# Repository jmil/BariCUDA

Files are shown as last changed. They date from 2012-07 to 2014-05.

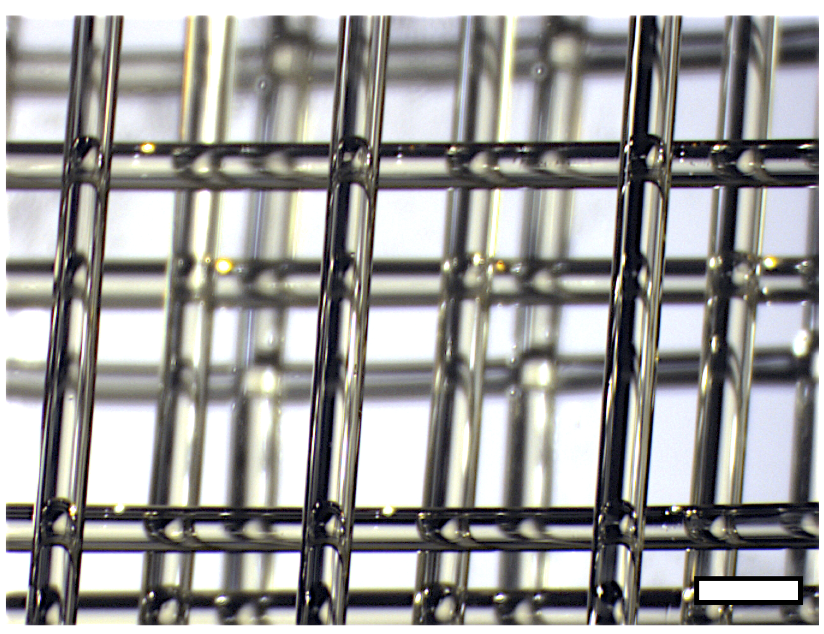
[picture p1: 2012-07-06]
MillerJS-03-3DPrintedSugar.png

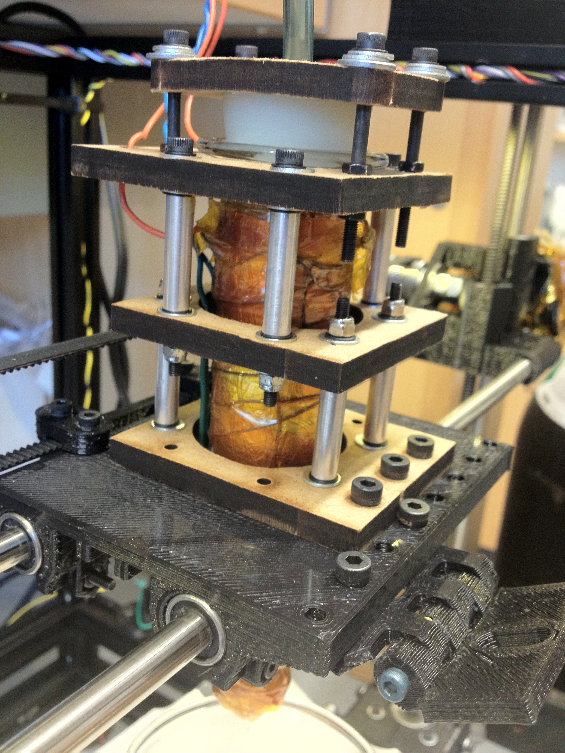
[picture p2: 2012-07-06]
SugarExtruder.jpg

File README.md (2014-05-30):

BariCUDA
========

License: GPL 3.0

BariCUDA -- air pressure driven (read BariC) Universal (it extrudes anything) Degree Amplifier (as in temperature)

by Jordan Miller http://twitter.com/jmil

As seen here:
http://www.thingiverse.com/thing:26343

See the BariCUDA used for precision pneumatic extrusion of sugar filaments for templating living vascular tissues for regenerative medicine:
http://www.youtube.com/watch?v=9VHFlwJQIkE

modified from MakerBot Frostruder MK2:
http://www.thingiverse.com/thing:1143

Introducing the BaricUDA Extruder.

Derived from the venerable MakerBot MK2 Frostruder, this air-pressure driven extruder ("baric") is a *U*niversal extruder because it adds a *D*egree *A*mplifier (yep... temperature) to let you extrude anything.

We used this to precisely extruder sugar templates for engineering vascular tissues for regenerative medicine research. See the details here:

You can use it for:
1) Molten Sugar Extrusion
2) Molten Chocolate Extrusion
3) Molten PLA and ABS and other experimental plastics Extrusion
3) Molten <insert your favorite thing here> Extrusion -- This is a *U*niversal Extruder! Any thermoplastic material can be extruded.

You are only limited by your motherboard and the number of MOSFETs you have (for control of pneumatics just like the Frostruder).

Operation is IDENTICAL to the Frostruder, you just need to add a heating element and thermistor for temperature measurement.

The Source Code and Files are Hosted on Github:
http://www.github.com/jmil/BariCUDA

NOTE: Sugar and Chocolate precision extrusion should be controlled NOT by precision of air pressure (which is hard) but instead by precision of temperature (which is easy). Temperature controls viscosity which controls extrusion rate at a given temperature.

The temperature to use depends on the material properties of your extrudate (read: the sugar). But you want around 100 degrees celsius extrusion for this type of sugar glass you can make at home (you DON'T need the cream of tartar):
http://www.wikihow.com/Make-Sugar-Glass

Chocolate is just as easy -- but don't use water! Chocolate and water don't mix.

RepRap does not support such a large extruder by default. You may need to first 3D print the additional Mendel vertices to widen the top of the Mendel so you can fit this extruder in there easily.

1. Get a Frostruder MK2 (you need the rubber stopper, tubing, and pneumatic solenoids)
2. Lasercut these new parts out of 1/4" MDF or other RIGID wood. It has to be really really stiff.
3. 3D print the RepRap holder for the extruder
4. Get the bolts, nuts, washers, and aluminum standoffs you need. I recommend locking nuts so that the fitting is tight.
5. Assemble and WIN!

NOTE: There's no BOM because it will depend on the thickness of the material you laser cut. I used 1/4" MDF and 50 mm screws with 25 mm aluminum standoffs. You should be able to figure it out by looking at the images in this Thing.

But the idea is you take the stopper clamp and top clamp and put the glass syringe in (I use Air-Tite.com). Then you wrap in foil and then wrap in nichrome and affix your thermistor. Then you put the stand-offs in and get the spacing you want with one or more spacer clamps. Then you should be all set.

I use one stopper clamp, one top clamp, one spacer clamp, and one bottom clamp.

The bottom clamp has the holes that affix it to the x-carriage on the RepRap. If you use 1/4" MDF it will be stiff enough to support the entire BariCUDA Extruder even while extruding. We have been using this design for more than a year and half with no problems.

Enjoy!

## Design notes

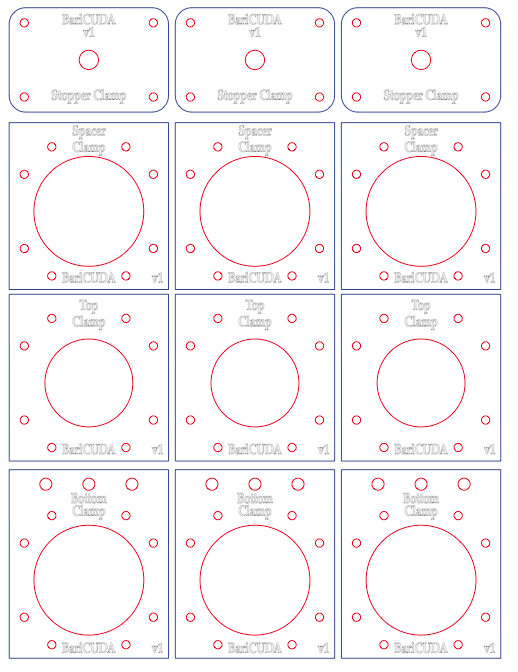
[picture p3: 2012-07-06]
jmil_Clamp_Screenshot.png

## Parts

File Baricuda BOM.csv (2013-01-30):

Part | Source | Part No. | Unit | Unit Price | Price | URL | Purpose/Notes
50 ft – 26 Gauge Nichrome 60 w/Double Glass Serve | pelicanwire | P2126N60DGS | 1 | 50 | 50
100 kOhm thermistor | ultimachine |  | 10 | 2.75 | 27.5 | http://ultimachine.com/content/thermistor-100k
2 pin terminal (crimping, soldering, stick in the hole) | ultimachine or OEDK |  | 1 | 2.5 | 2.5 | http://ultimachine.com/content/254mm-1x2-connector-housing-kit-6-pack | connecting thermistor to motherboard
25 - Zinc-Plated Alloy Steel M3 50 mm screws | McMaster Carr | 91290A137 | 4 | 4.91 | 19.64 | http://www.mcmaster.com/#catalog/118/3121/=j61hb4
100 - Zinc-Plated Alloy Steel M3 20 mm screws | McMaster Carr | 91290A123 | 1 | 6.47 | 6.47 | http://www.mcmaster.com/#catalog/118/3121/=j61hb4
Al Standoffs, 25mm, fits M3 | McMaster Carr | 94669A027 | 8 | 1.5 | 12 | http://www.mcmaster.com/#catalog/118/3257/=j61kk1
50 - Metric Type 316 SS Nylon-Insert Hex Locknut M3 Size, .5mm Pitch, 5.5mm Width, 4mm Height | McMaster Carr | 94205A220 | 4 | 4.75 | 19 | http://www.mcmaster.com/#catalog/118/3197/=j6ajwr
50 - M3 Metric Hex Nuts | McMaster Carr | 94150A325 | 2 | 3.08 | 6.16 | http://www.mcmaster.com/#94150A325
100 - 316 Stainless Steel M3 Washers | McMaster Carr | 90965A130 | 1 | 1.76 | 1.76 | http://www.mcmaster.com/#90965A130
100 - 316 Stainless Steel M4 Washers | McMaster Carr | 90965A150 | 1 | 2.43 | 2.43 | http://www.mcmaster.com/#90965A150
50 - 316 Stainless Steel M4 nuts | McMaster Carr | 94150A335 | 2 | 3.42 | 6.84 | http://www.mcmaster.com/#94150A335
100 - 12.9 Alloy Steel M4 25 mm screws | McMaster Carr | 91290A176 | 1 | 8.14 | 8.14 | http://www.mcmaster.com/#91290A176
Air-tite 50 mL glass syringe | Air-Tite | GL50 | 1 | 31.95 | 31.95 | http://www.air-tite-shop.com/p-34-glass-syringe-metal-luer-lock-tip.aspx
silicone or rubber stopper (#8 or #9 size) | Chem Stockroom |  |  |  | 0
18 gauge steel nozzle luer lock | Nordson EFD - custom quote | KIT, TIP 18GA .033"(.84MM)X1/2" SS, 5PC | 1 | 36.54 | 36.54
1/4” wide Kapton Tape | ultimachine | UMKPTON025 | 5 | 8 | 40 | http://ultimachine.com/content/dupont-kapton-high-temp-adhesive-tape-14
1' Ceramic Insulation Tape | ultimachine | UMCERTAPE | 5 | 1.5 | 7.5 | http://ultimachine.com/content/ceramic-insulation-tape
3 Way 2 Position Solenoid Air Valve 1/4" NPT 12V DC | ebay | Item# 190444504454 | 1 | 29.84 | 29.84 | http://cgi.ebay.com/ws/eBayISAPI.dll?ViewItem&item=190444504454 | only works at 10-20 psi minimum, but CHEAP!
10 – PC Swift Push Lock Straight Fittings 1/4"OD- 1/4"NPT | ebay | Item# 260477680739 | 1 | 7.8 | 7.8 | http://cgi.ebay.com/ws/eBayISAPI.dll?ViewItem&item=260477680739
1/4" polyurethane Tubing |  | Item # 260505968939 | 1 | 22.35 | 22.35 | http://cgi.ebay.com/ws/eBayISAPI.dll?ViewItem&item=260505968939
tube cutter |  | Item # 260489803800 | 1 | 6.7 | 6.7 | http://cgi.ebay.com/ws/eBayISAPI.dll?ViewItem&item=260489803800
0.5" acrylic from pattern (laser cut) | MW has extra material |  |  |  | 0
25 – 12.9 Alloy Steel M3 40mm socket head screws | McMaster Carr | 92290A128 | 2 | 3.63 | 7.26 | http://www.mcmaster.com/#socket-head-cap-screws/=j6anv3
 |  |  |  |  | 0
X-CARRIAGE |  |  |  |  | 0
4 of 8 mm LM8UU linear bearings | Ebay |  | 1 | 7 | 7 | http://www.ebay.com/itm/10pcs-LM8UU-8mm-Linear-Ball-Bearing-Bush-Bushing-/290638920863?pt=LH_DefaultDomain_0
4 25 mm m3 screws and nuts | McMaster Carr |  |  |  |  |  | covered in above lines
Printed X-Carriage Part | MW has material
 |  |  |  | TOTAL | 359.38

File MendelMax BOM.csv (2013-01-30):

PLEASE NOTE: A kit with all items marked with an X or "Upgraded" in column C is available from http://store.mendelmax.com/mendelmax-hardware-kit/
Item | Category | In MM.com kit | Part Number | Source | Qty Required for build | Order qty of pt number | Price Each | extended | Needed for | Notes
10mm M5-.80 screws, bag of 100 | Hardware | x | 91292A124 | McMaster | 100 | 1 | $7.68 | $7.68 | MendelMax | You need exactly 100 of these screws for a standard build, so I recommend you buy a spare bag. If you only get one bag, you can probably source individual replacement screws at Fastenal or another local source, but they are at a substantial premium. You will almost certainly need spares to add accessories. I prefer stainless steel for purely aesthetic reasons, but you can save a couple dollars by using Zinc or Black Oxide. I recommend Socket Head screws, but phillips or other M5-.8 machine screws will also work, but they are more fiddly to assemble.
608ZZ Bearings | bearings | x | 608ZZ10 | VXB.com | 7 | 7 | $0.50 | $3.50 | MendelMax | 2 each are used for the X & Y idlers, 3 for the Wade's extruder. You will also need four if you use the suggested filament spool. Part number is for a 10 pack for $5, you may want to buy a larger package, these bearings are used in many reprap related projects.
8mm Thrust Bearing | bearings | Not needed | 6655K54 | McMaster | 2 | 2 | $2.79 | $5.58 | MendelMax | These are optional, and are used to support the weight of the Z axis from the base of the printer, instead of from the motor shafts. This should improve reliability and extend motor life. You can safely leave these off if you prefer, and there is little benefit if you are using high quality Z couplers.
8mm Drill Rod 36" or 1M | hardware | upgraded | 88625K67 | McMaster | 3 | 3 | $5.13 | $15.39 | MendelMax | You can use 8mm or 5/16", and any formula of drill rod (Called "Silver Steel" in some parts of the world). Type O1 or W1 is usually cheapest and are perfectly suited to what we need. Stainless is also fine, but is considerably more expensive. Plain steel rods from a hardware store are not recommended, and zinc coated rods are not suitable.
M3 or SAE #6 washers | hardware | x | 90126A509 | McMaster | 20 | 1 | $1.27 | $1.27 | MendelMax | McMaster part is for a box of 100. Single parts are likely at least $.05 each, so it is most cost effective to just buy 100.
Wade's Idler Stud | hardware |  | 90435A120 | McMaster | 1 | 1 | $0.30 | $0.30 | Wade's | Not required if you have a cutoff of M8 from your threaded rod, but for $.32 saves the effort of an extra cut.
M5 nuts, box of 100 (Thin nuts preferred) | hardware | x | 90695A037 | McMaster | 1 | 1 | $2.78 | $2.78 | MendelMax | You only need a few for the assembly, but it is best to buy 100. Zinc coated is fine. Thin nuts are preferable to normal nuts since they can be used in place of t-slot nuts in a pinch, and even used as post-install nuts (they can be inserted through the top of the slot after the bot is assembled).
M3-.50, 10mm long | hardware | x | 91290A115 | McMaster | 20 | 1 | $4.48 | $4.48 | MendelMax | McMaster part is for a box of 100. Single parts are likely at least $.25 each, so it is most cost effective to just buy 100.
20-25mm M5 screws | hardware | x | 91292A128 | McMaster | 8 | 1 | $0.25 | $0.25 | MendelMax | You need 8, but I recommend just getting a box, they will be handy for future projects. Again, Stainless and the screw head type are specified only for looks, any similar screw will work.
M5 or #10 Washers, box of 100 | Hardware | x | 92141A011 | McMaster | 84 | 1 | $2.33 | $2.33 | MendelMax | Either M5 or SAE #10 washers will work. I use SAE #10 because they are slightly cheaper in the US. I use stainless for purely aesthetic reasons.
8mm or 5/16" threaded rod, 36" or 1M | hardware | upgraded | 98847A030 | McMaster | 1 | 1 | $3.89 | $3.89 | MendelMax | Plain steel or stainless will work, but stainless is recommended. Do not use zinc coated rod, as the zinc can lead to binding.
GT2 Belt | Belts | x | A 6R51M497060 | SDP-SI.com | 2 | 2 | $6.81 | $13.62 | MendelMax | Suitable pulleys & belts are also available from Misumi, but are considerably more expensive.
GT2 Pulleys | Belts | x | A 6Z51M036DF0605 | SDP-SI.com | 2 | 2 | $5.84 | $11.68 | MendelMax
Linear Bushings | bearings | x | A 7Z44MPSD08MAF | SDP-SI.com | 12 | 12 | $1.48 | $17.76 | MendelMax | After much debate, I have switched the recommended bushings from the previous Igus bushings, to a much easier to use Self Aligning bushing from SDP. Thease are a bit more expensive, but they are basicalaly foolproof, whereas the Igus bushings required a fairly high-precision mounting block that was difficult to reproduce accurately on a RepRap. MANY other choices are available, including LM8UU's, printed bushings, etc, but this is a good, inexpensive bushing that is very well suited to our application. Please note, SDP offers similar Bronze bushings that are a great choice with precision linear shafting, but are not recommended with drill rod.
300mm extrusions | Extrusions | x | HFS5-2020-300 | Misumi | 4 | 4 | $1.71 | $6.84 | MendelMax
340mm Extrusions | Extrusions | x | HFS5-2020-340 | Misumi | 4 | 4 | $1.93 | $7.72 | MendelMax
420mm extrusions | Extrusions | x | HFS5-2020-420 | Misumi | 6 | 6 | $2.39 | $14.34 | MendelMax
T-Slot nuts, bag of 100 | Extrusions | x | HNKK5-5 | Misumi | 1 | 1 | $19.32 | $19.32 | MendelMax
Blind Joint Screws | Extrusions | x | HTJ5 | Misumi | 4 | 4 | $0.62 | $2.48 | MendelMax
Pololu A4988 Stepper driver | electronics |  | http://www.lulzbot.com/en/24-pololu-a4988-stepper-motor-driver.html | Lulzbot.com | 4 | 4 | $16.00 | $64.00 | RAMPS | Also available from Pololu.com or Ultimachine.com. You need four, but having a spare on hand is not a bad idea.
NEMA 17 Motor | motors |  | http://www.lulzbot.com/en/48-nema-17-stepper-motors.html | lulzbot.com | 4 | 4 | $18.00 | $72.00 | MendelMax | http://ultimachine.com/content/kysan-1124090-nema-17-stepper-motor is also suitable. Desired specs: NEMA17 size, 1.5A or less, 8 mH inductance or less, 62oz.in (44Ncm, 4.4kg.cm) or more of torque, 1.8 or 0.9 degrees per step (200/400 steps/rev respectively)
RAMPS electronics | electronics |  | http://www.lulzbot.com/en/49-ramps-14-assembled.html | Lulzbot.com | 1 | 1 | $85.00 | $85.00 | RAMPS | Ultimachine.com is also an excellent choice
1" heat proof spacers | hardware | Not needed |  | hardware store | 4 | 4 | $0.25 | $1.00 | Y-axis | Used to rigidly separate the top and bottom plate, Should be heat resistant and preferably not heat conductive. I use hardwood.
12V 30A power Supply | Electronics |  |  | ebay | 1 | 1 | $37.00 | $37.00 |  | 30A is WAY more than you need, even with a 12V Heated Build Platform, but it should last longer if used well under it's specified rating, and the difference in price for an extra 10A is only about $10. You can safely use anything as low as 12V 6A with a 120V HBP and 15A with a 12V HBP. http://www.ebay.com/itm/New-12V-DC-30A-350W-Regulated-Switching-Power-Supply-MW-/120692623020?pt=LH_DefaultDomain_0 is a known good US seller, but there are other options on ebay that may be better for international buyers. Search for "12V 30A power supply". With a 30A supply, I happily run two RepRaps from a single power supply.
Aluminum sheet, 9..75x6x0.1" or 1/8" | Metal | Upgraded |  | OnlineMetals.com | 1 | 1 | $7.02 | $7.02 | Y-axis | Y-axis carriage plate, see above.
Aluminum sheet, 9.75x11x0.1" or 1/8" | Metal | x |  | OnlineMetals.com | 1 | 1 | $12.87 | $12.87 | Y-axis | Y-axis table, scale as needed. May be cheaper if sourced locally. Other materials are possible, but this is my preferred table design. Alloy is irrelevant, the quoted price is for 3003, which is usually the cheapest.
Arduino MEGA 1280 or 2560 | electronics |  |  | ebay.com | 1 | 1 | $30.00 | $30.00 | RAMPS | Either the 1280 or 2560 works fine, I recommend the 1280.
Heated Build Platform | Electronics | Upgraded |  | Ultimachine.com | 1 | 1 | $50.00 | $50.00 | Y Axis | The MendelMax has a slightly larger buld area than a Prusa, but you can use a standard Prusa HBP screwed to the bottom of an aluminum heat spreader. Using a Silicone heater such as McMaster #35765K55 works great too, but requires some expert advice, so consult #mendelMax before ordering.
Hobbed bolt | hardware |  |  | lulzbot.com | 1 | 1 | $7.00 | $7.00 | Wade's | It is possible to DIY as well, but for $7 it is not worth the effort.
Hot End | Hot End |  |  | Makergear | 1 | 1 | $75.00 | $75.00 | MendelMax | http://www.makergear.com/products/operators-pack I recommend the .5mm for 3mm filament to start with.
M5-30mm screws | hardware | x | 92125A220 ($7.85 for 25pk) (McMaster Carr) | hardware store | 4 | 4 | $0.30 | $1.20 | Y-axis | Used to connect the two plates. I recommend flat head screws, but you will need to countersink your top plate to use these. You can buy a countersink at your local hardware store. These allow you to set the screw tops flush with the table surface so you will not crash into the screws.
M8 or 5/16" Nuts | hardware | x | Square: 96887A322 ($5 for 25 pk) Hex: 91828A410 ($9.98 for 50pk) | Hardware store | 8 | 8 | $0.25 | $2.00 | MendelMax | Any suitable nuts from your local hardware store. Do not use Zinc coated, either plain steel or stainless is fine, and the material does not need to match your rods.
M8 or 5/16" screw or bolt, 25-30mm long | hardware | x | 91292A192 ($6.35 for 50) | Hardware store | 2 | 2 | $0.50 | $1.00 | MendelMax | Used to mount the the idler bearings on the X & Y axes. You may be able to use leftovers of your threaded rod, in which case you will need two extra nuts above. In the US, you can get these at Fastenal for $0.48 each: http://www.fastenal.com/web/products/detail.ex?sku=73496&ucst=t Again, I use Stainless for aesthetic reasons, but any finish or type of screw will work here as long as it is the right size.
M8 or 5/16" washers | Hardware | x | 90126A030 | hardware store | 4 | 4 | $0.25 | $1.00 |  | Used for the idlers. If you build the optional filament spool mount you will need an additional four.
NEMA 17 Motor | motors |  |  | lulzbot.com | 1 | 1 | $18.00 | $18.00 | Wade's | An additional stepper is required if you are using a Wade's extruder.
Printed Parts | RP |  |  |  | 1 | 1 | $85.00 | $85.00 | MendelMax | Lulzbot.com is selling sets, other sources should be available as well. http://www.lulzbot.com/en/plastic-parts/61-mendelmax-plastic-parts.html
Wade's extruider hardware | hardware |  |  | Hardware store | 1 | 1 | $5.00 | $5.00 | Wade's | Misc hardware required by the Wade;s extruder. Since you only need one or two of each, it is best to source these locally. See http://reprap.org/wiki/Wade%27s_Geared_Extruder for the full list. The bearings, hobbed bot (m8-50mm) and the screws and washers for the motor are already in this list.
Z Shaft couplers | hardware | x |  | ebay.com | 2 | 2 | $5.00 | $10.00 | MendelMax | http://www.ebay.com/itm/CNC-5x8mm-Motor-Shaft-Coupler-5mm-8mm-Coupling-/180707733213?pt=LH_DefaultDomain_0 You can also print your own couplers, but I have found printed couplers are considerably less reliable. Printed couplers should work much better if you use the thrust bearings listed above.
 |  |  |  |  |  |  |  | $515.00
 |  |  |  |  |  |  |  | $0.00
 |  |  |  |  |  |  |  | $0.00
 |  |  |  |  |  |  |  | $0.00
MendelMax 1.5 |  |  |  |  |  |  |  | $0.00
Item Number | Quantity | Part Number | Part Name | Configuration Name | Part Type | Revision | Comment | $0.00
1 | 4 |  | 608zz |  | Hardware |  |  | $0.00
2 | 2 |  | Acme_Leadscrew |  | Hardware |  |  | $0.00
3 | 2 |  | Bearing_Mount |  | Laser Cut |  |  | $0.00
4 | 2 |  | Cross Member |  | Laser Cut |  |  | $0.00
5 | 4 |  | HFS5-2020-300 |  | Extrusion |  |  | $0.00
6 | 4 |  | HFS5-2020-340 |  | Extrusion |  |  | $0.00
7 | 6 |  | HFS5-2020-420 |  | Extrusion
8 | 1 |  | Insulation |  | Hardware
9 | 2 |  | Insulation Clip |  | Laser Cut
10 | 2 |  | Lower Vertex Lower | Right | RP
11 | 2 |  | Lower Vertex Lower | Left | RP
12 | 2 |  | Lower Vertex Upper | Right | RP
13 | 2 |  | Lower Vertex Upper | Left | RP
14 | 12 |  | m3 no6 washer |  | Hardware
15 | 14 |  | m3 Socket Head Cap Screw | 10mm | Hardware
16 | 94 |  | m5 Socket Head Cap Screw | 10mm | Hardware
17 | 4 |  | m5 Socket Head Cap Screw | 22mm | Hardware
18 | 2 |  | m5 Socket Head Cap Screw | 12mm | Hardware
19 | 9 |  | m5 Socket Head Cap Screw | 20mm | Hardware
20 | 90 |  | m5_no10_washer |  | Hardware
21 | 4 |  | m5-10 flat head |  | Hardware
22 | 2 |  | m5-m6_35mm coupler |  | Hardware
23 | 66 |  | m5-misumi nut-hnkk5-5 |  | Hardware
24 | 29 |  | M5-thin nut |  | Hardware
25 | 3 |  | M8 Washer |  | Hardware
26 | 2 |  | m8-30 |  | Hardware
27 | 2 |  | M8-nut |  | Hardware
28 | 2 |  | MendelMax Leadscrew Nut |  | Hardware
29 | 1 |  | MendelMax Table |  | Custom
30 | 4 |  | NEMA17_47mm_deep |  | Motors
31 | 1 |  | Rod_mount_fixed |  | Laser Cut
32 | 1 |  | Rod_mount_float |  | Laser Cut
33 | 4 |  | Self Aligning Bushing | 10mm | Hardware
34 | 12 |  | Self Aligning Bushing | 8mm | Hardware
35 | 2 |  | Shaft, 10mm | 405mm | Hardware
36 | 2 |  | Shaft, 8mm | 445mm | Hardware
37 | 2 |  | Shaft, 8mm | 420mm | Hardware
38 | 1 |  | Silicone Heater |  | Electronics
39 | 2 |  | Table Support |  | Laser Cut
40 | 2 |  | Table_attachment |  | Laser Cut
41 | 2 |  | Top_Vertex_X | Logo | RP
42 | 2 |  | Top_Vertex_X | No Logo | RP
43 | 1 |  | X End Clamp for MendelMax Leadscrew |  | RP
44 | 1 |  | X End Idler for MendelMax Leadscrew |  | RP
45 | 1 |  | X End Motor for MendelMax Leadscrew |  | RP
46 | 1 |  | Y_Motor_Mount |  | RP
47 | 1 |  | Y-Idler-mount |  | RP
48 | 1 |  | Y-Idler-tensioner |  | RP
19 | 1 |  | Y-rod_mount_jig |  | Laser Cut
50 | 2 |  | Z_lower_motor_mount_10mm |  | RP
51 | 2 |  | Z_lower_motor_mount_10mm_support | Normal | RP
52 | 2 |  | Z_lower_motor_mount_10mm_support | Mirrored | RP
53 | 4 |  | Z_rod_clasp |  | RP
54 | 2 |  | Z_Top_Vertex_10mm_New |  | RP

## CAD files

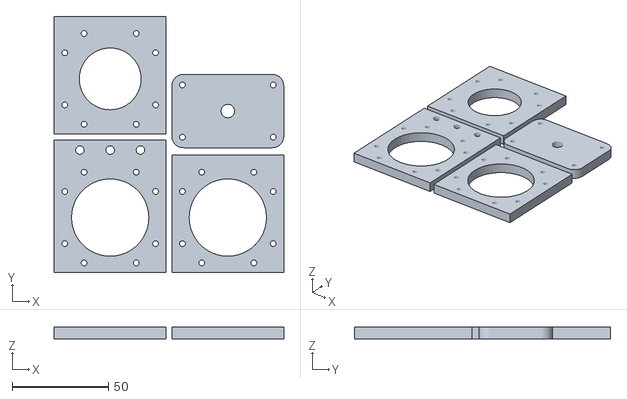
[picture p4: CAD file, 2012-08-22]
Baricuda_v1_LaserCutParts.stl
119.1 x 132.7 x 6.00

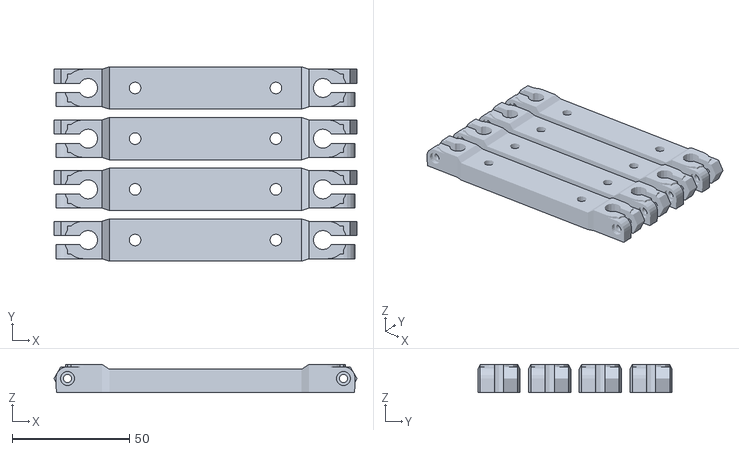
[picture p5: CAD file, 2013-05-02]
modifiedMendelMax1.5/Compact_MendelMax_Y-Rod_Holders/jmilYRodHolderfor8mmSmoothRods4off_fixed.stl
129.1 x 82.8 x 12.0

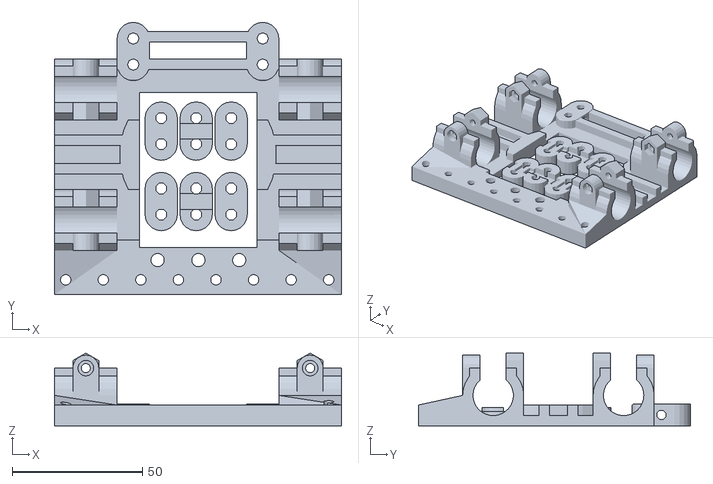
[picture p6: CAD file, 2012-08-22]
BariCUDA RepRap Holder with Fan Mount.stl
110.0 x 104.4 x 27.9

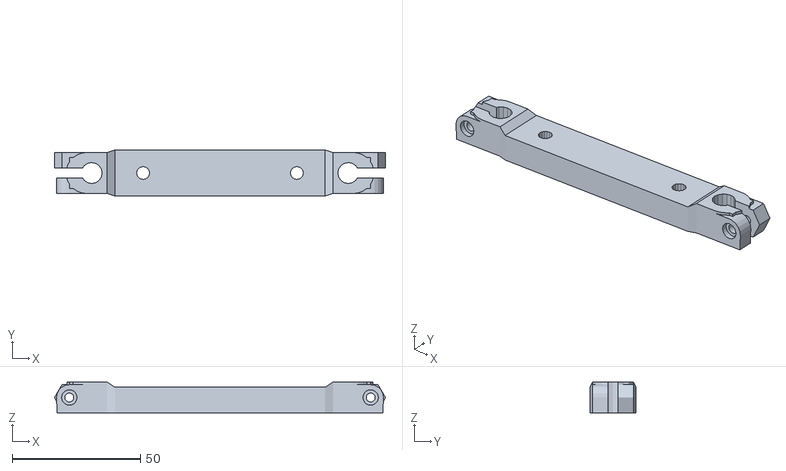
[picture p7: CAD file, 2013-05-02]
modifiedMendelMax1.5/Compact_MendelMax_Y-Rod_Holders/jmilYRodHolderfor8mmSmoothRods_fixed.stl
129.1 x 18.0 x 12.0

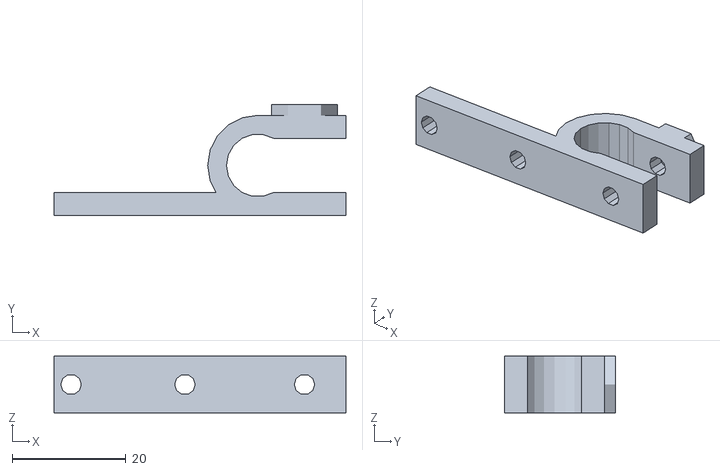
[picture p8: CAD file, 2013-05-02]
modifiedMendelMax1.5/endstop-holder_10mm.stl
51.3 x 19.5 x 10.0

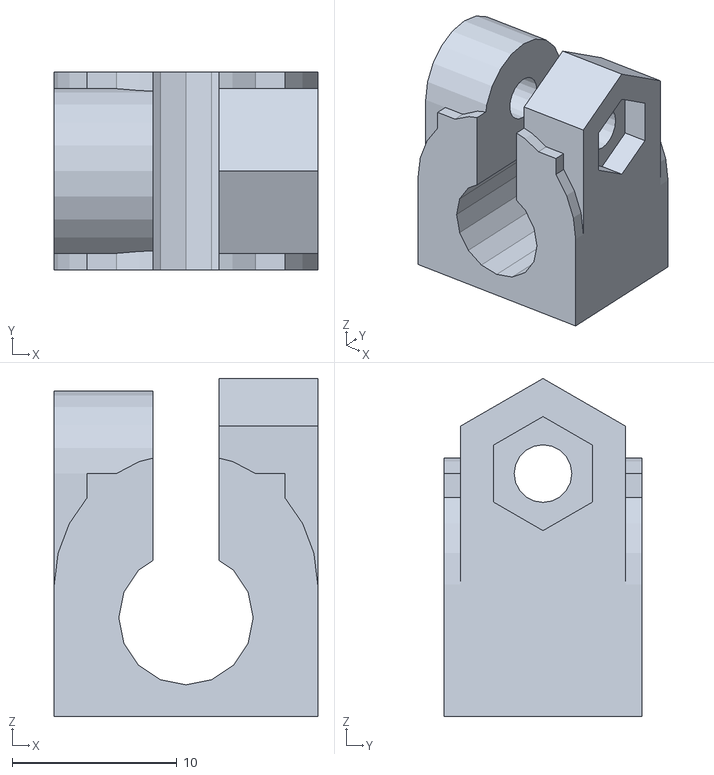
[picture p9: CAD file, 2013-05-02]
modifiedMendelMax1.5/Compact_MendelMax_Y-Rod_Holders/lm8uu-holder-slim_v1-1_for8mmSmoothRods.stl
16.0 x 12.0 x 20.5

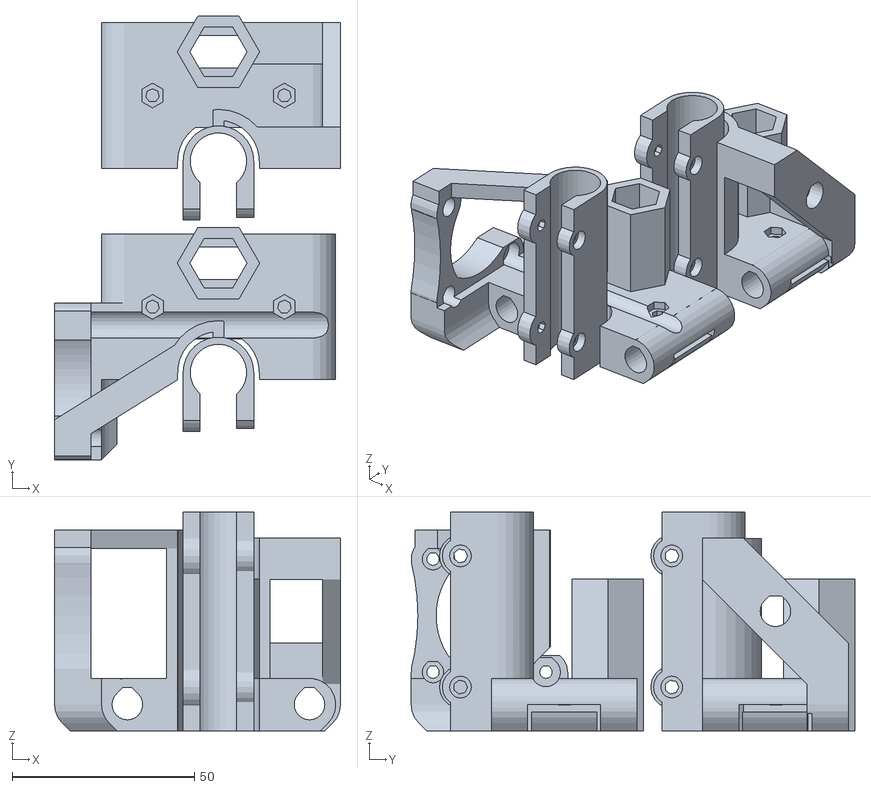
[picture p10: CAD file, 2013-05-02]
modifiedMendelMax1.5/jonaskuehlingxendsthreadedRod_fixed.stl
78.5 x 121.8 x 60.0

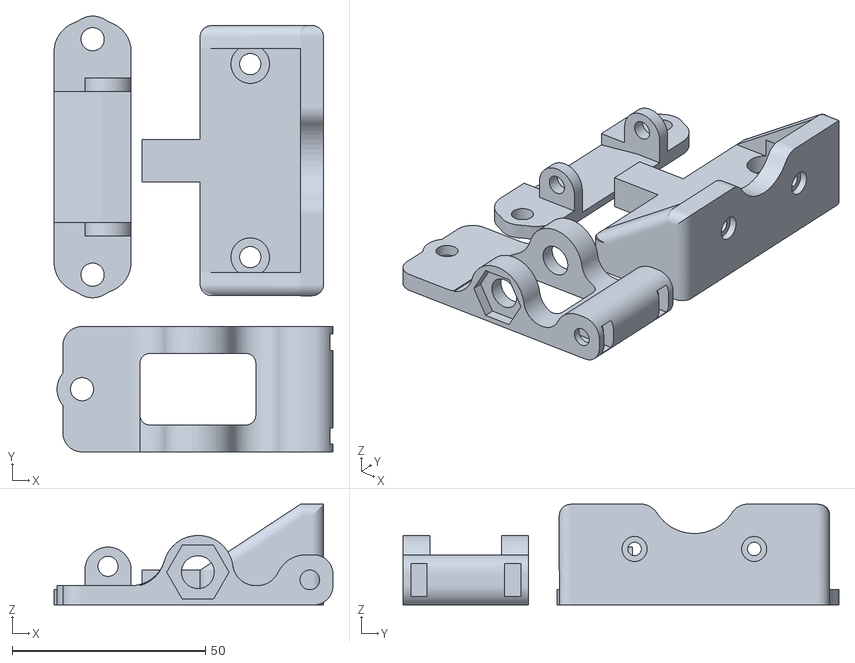
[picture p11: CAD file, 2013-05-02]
modifiedMendelMax1.5/jmilPlate-MendelMax1.5--YaxisOnly.stl
72.3 x 112.9 x 26.1

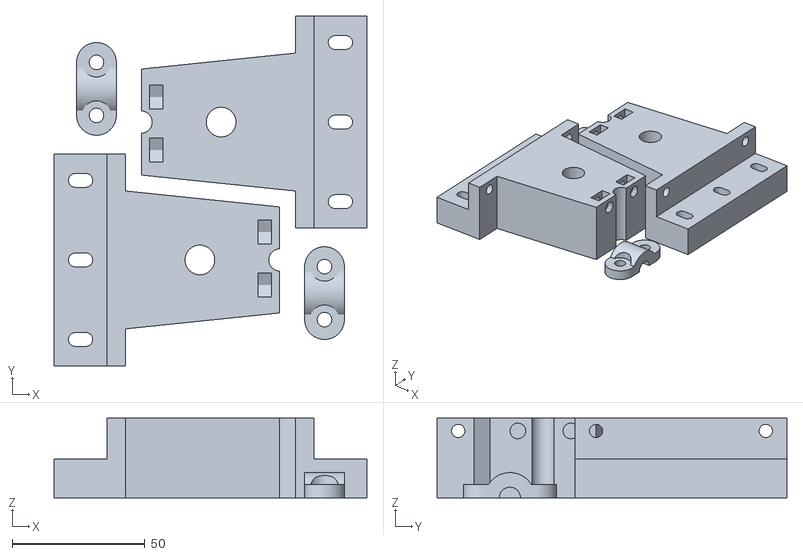
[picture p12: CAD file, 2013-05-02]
modifiedMendelMax1.5/jmilImprovedZUpperIdlerMount2off_fixed.stl
118.0 x 132.0 x 30.0

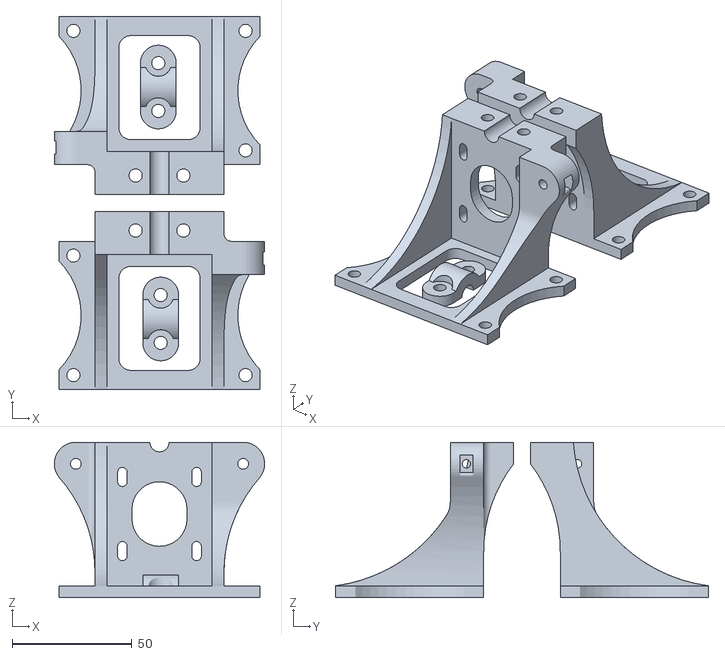
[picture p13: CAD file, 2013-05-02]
modifiedMendelMax1.5/jmil_ImprovedZ-LowerMotorMounts.stl
88.0 x 156.0 x 65.0

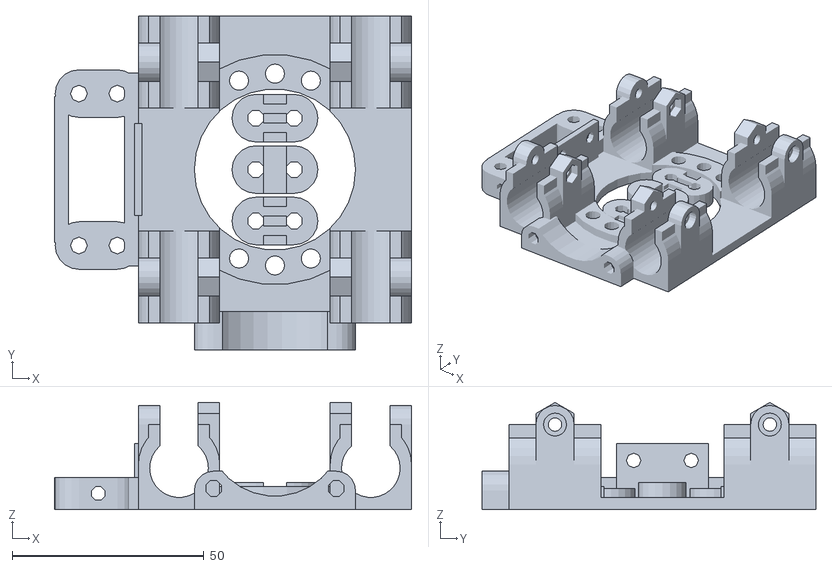
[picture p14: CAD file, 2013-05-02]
modifiedMendelMax1.5/X-carriage_slim_lm8uu_MendelMax.stl
93.1 x 87.0 x 27.9

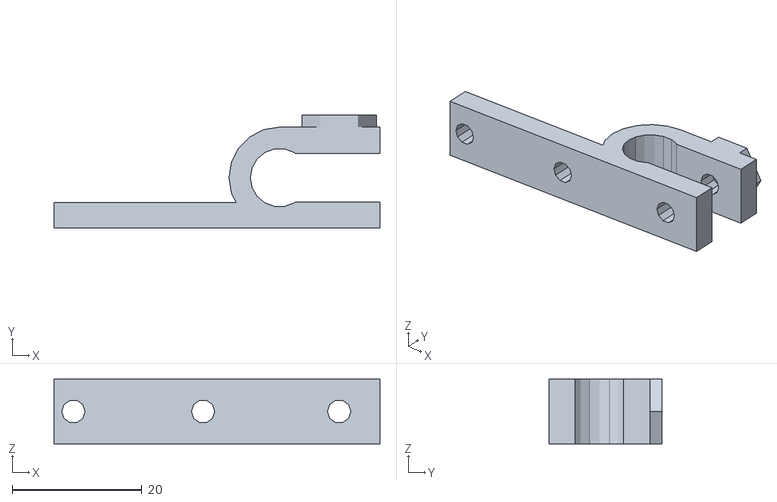
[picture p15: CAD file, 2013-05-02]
modifiedMendelMax1.5/endstop-holder_8mm.stl
50.3 x 17.5 x 10.0

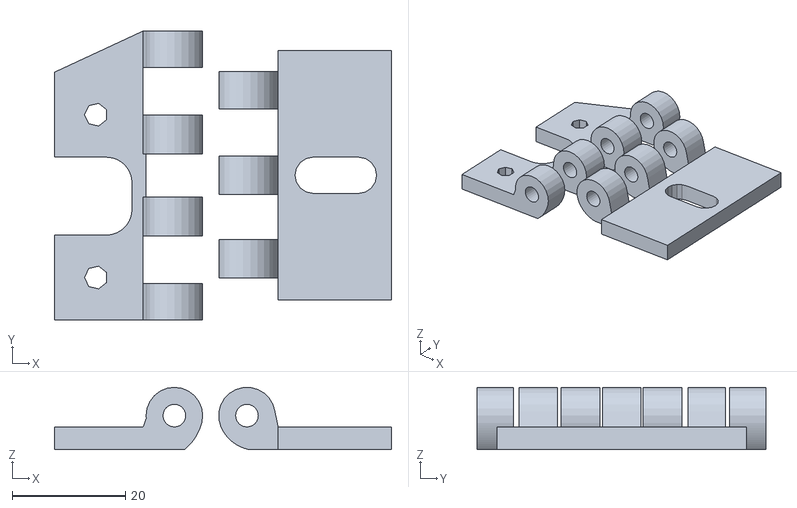
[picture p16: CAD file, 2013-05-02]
modifiedMendelMax1.5/CAMERAMountWithScrewHolejmil_fixed.stl
59.5 x 51.0 x 11.0

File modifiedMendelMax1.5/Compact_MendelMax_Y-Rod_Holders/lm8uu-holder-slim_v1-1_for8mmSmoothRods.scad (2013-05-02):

// LM8UU holder slim v1.1
// *********************************************
// Jonas Kühling
// http://www.jonaskuehling.de
// http://www.thingiverse.com/jonaskuehling
// *********************************************
// derived from:
// http://www.thingiverse.com/thing:14942

// LM8UU/rod dimensions
LM8UU_dia = 8;
LM8UU_length = 12;
rod_dia = 2;

//screw/nut dimensions (M3) - hexagon socket head cap screw ISO 4762, hexagon nut ISO 4032
screw_thread_dia_iso = 3;
screw_head_dia_iso = 5.5;
nut_wrench_size_iso = 5.5;


// screw/nut dimensions for use (plus clearance for fitting purpose)
clearance_dia = 0.5;
screw_thread_dia = screw_thread_dia_iso + clearance_dia;
screw_head_dia = screw_head_dia_iso + clearance_dia;
nut_wrench_size = nut_wrench_size_iso + clearance_dia;
nut_dia_perimeter = (nut_wrench_size/cos(30));
nut_dia = nut_dia_perimeter;
nut_surround_thickness = 2;

// main body dimensions
body_wall_thickness = 4;
body_width = LM8UU_dia + (2*body_wall_thickness);
body_height = body_width;
body_length = LM8UU_length;
gap_width = rod_dia + 2;
screw_bushing_space = 1;
screw_elevation = LM8UU_dia + body_wall_thickness + (screw_thread_dia/2) +screw_bushing_space;

// TEST - uncomment to render in openscad:
// lm8uu_holder(1);		// WITH mountplate
 lm8uu_holder();		// WITHOUT mountplate


// nophead's polyhole module for better lm8uu-fit
module polyhole(d,h) {
    n = max(round(2 * d),3);
    rotate([0,0,180])
        cylinder(h = h, r = (d / 2) / cos (180 / n), $fn = n);
}


module mount_plate()
{
	difference()
	{
		translate([0,0,1.5])
		cube([body_width+2*screw_head_dia+4*nut_surround_thickness,screw_head_dia+2*nut_surround_thickness,3], center=true);

		for(i=[-1,1])
			translate([i*(body_width/2+nut_surround_thickness+screw_head_dia/2),0,-0.5])
				cylinder(r=screw_thread_dia/2, h=4, $fn=20);
	}
}

// main body
module lm8uu_holder(with_mountplate=false)
{
	difference()
	{
		union()
		{
			if (with_mountplate) 
			mount_plate();
	
			// body
			translate([0,0,body_height/4])
				cube([body_width,body_length,body_height/2], center=true);
			translate([0,0,(LM8UU_dia/2)+body_wall_thickness])		
				rotate([90,0,0])
					cylinder(r=(LM8UU_dia/2)+body_wall_thickness, h=LM8UU_length, center=true);
	
			// gap support
			translate([-(gap_width/2)-body_wall_thickness,-(body_length/2),body_height/2])
				cube([body_wall_thickness,LM8UU_length,(LM8UU_dia/2)+screw_bushing_space+(screw_thread_dia/2)]);
			translate([gap_width/2,-(body_length/2),body_height/2])
				cube([body_wall_thickness,LM8UU_length,(LM8UU_dia/2)+screw_bushing_space+(screw_thread_dia/2)]);
	
	
			// nut trap surround
			translate([gap_width/2,0,screw_elevation])
				rotate([0,90,0])
					cylinder(r=(((nut_wrench_size+nut_surround_thickness*2)/cos(30))/2), h=(body_width-gap_width)/2, $fn=6);
			translate([gap_width/2+(body_width-gap_width)/4,0,screw_elevation/2])
				cube([(body_width-gap_width)/2,nut_wrench_size+(nut_surround_thickness*2),screw_elevation],center=true);

			// Screw hole surround
			translate([-gap_width/2,0,screw_elevation])
				rotate([0,-90,0])
					cylinder(r=(screw_head_dia/2)+nut_surround_thickness, h=(body_width-gap_width)/2, $fn=20);
			translate([-(gap_width/2+(body_width-gap_width)/4),0,screw_elevation/2])
				cube([(body_width-gap_width)/2,screw_head_dia+(nut_surround_thickness*2),screw_elevation],center=true);
		}
	
		// bushing hole
		translate([0,0,LM8UU_dia/2+2])
			rotate([90,0,0])
//				cylinder(r=LM8UU_dia/2, h=LM8UU_length+1, center=true);
				translate([0,0,-(LM8UU_length+1)/2]) polyhole(LM8UU_dia,LM8UU_length+1);	// TESTING POLYHOLE MODULE FOR BETTER LM8UU FIT
	
		// top gap
		translate([-(gap_width/2),-(body_length/2)-1,body_height/2])
			cube([gap_width,LM8UU_length+2,(LM8UU_dia/2)+screw_bushing_space+(screw_thread_dia/2)+(nut_dia/2)+nut_surround_thickness+1]);
	
		// screw hole (one all the way through)
		translate([0,0,screw_elevation])
			rotate([0,90,0])
				cylinder(r=screw_thread_dia/2, h=body_width+3, center=true, $fn=20);
	
		// nut trap
		translate([gap_width/2+body_wall_thickness,0,screw_elevation])
			rotate([0,90,0])
				cylinder(r=nut_dia/2, h=body_width/2-gap_width/2-body_wall_thickness+1,$fn=6);
	
		// screw head hole
		translate([-(gap_width)/2-body_wall_thickness,0,screw_elevation])
			rotate([0,-90,0])
				cylinder(r=screw_head_dia/2, h=body_width/2-gap_width/2-body_wall_thickness+1,$fn=20);
	
	}
}

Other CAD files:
CAMERAMountWithScrewHole_jmil.stl

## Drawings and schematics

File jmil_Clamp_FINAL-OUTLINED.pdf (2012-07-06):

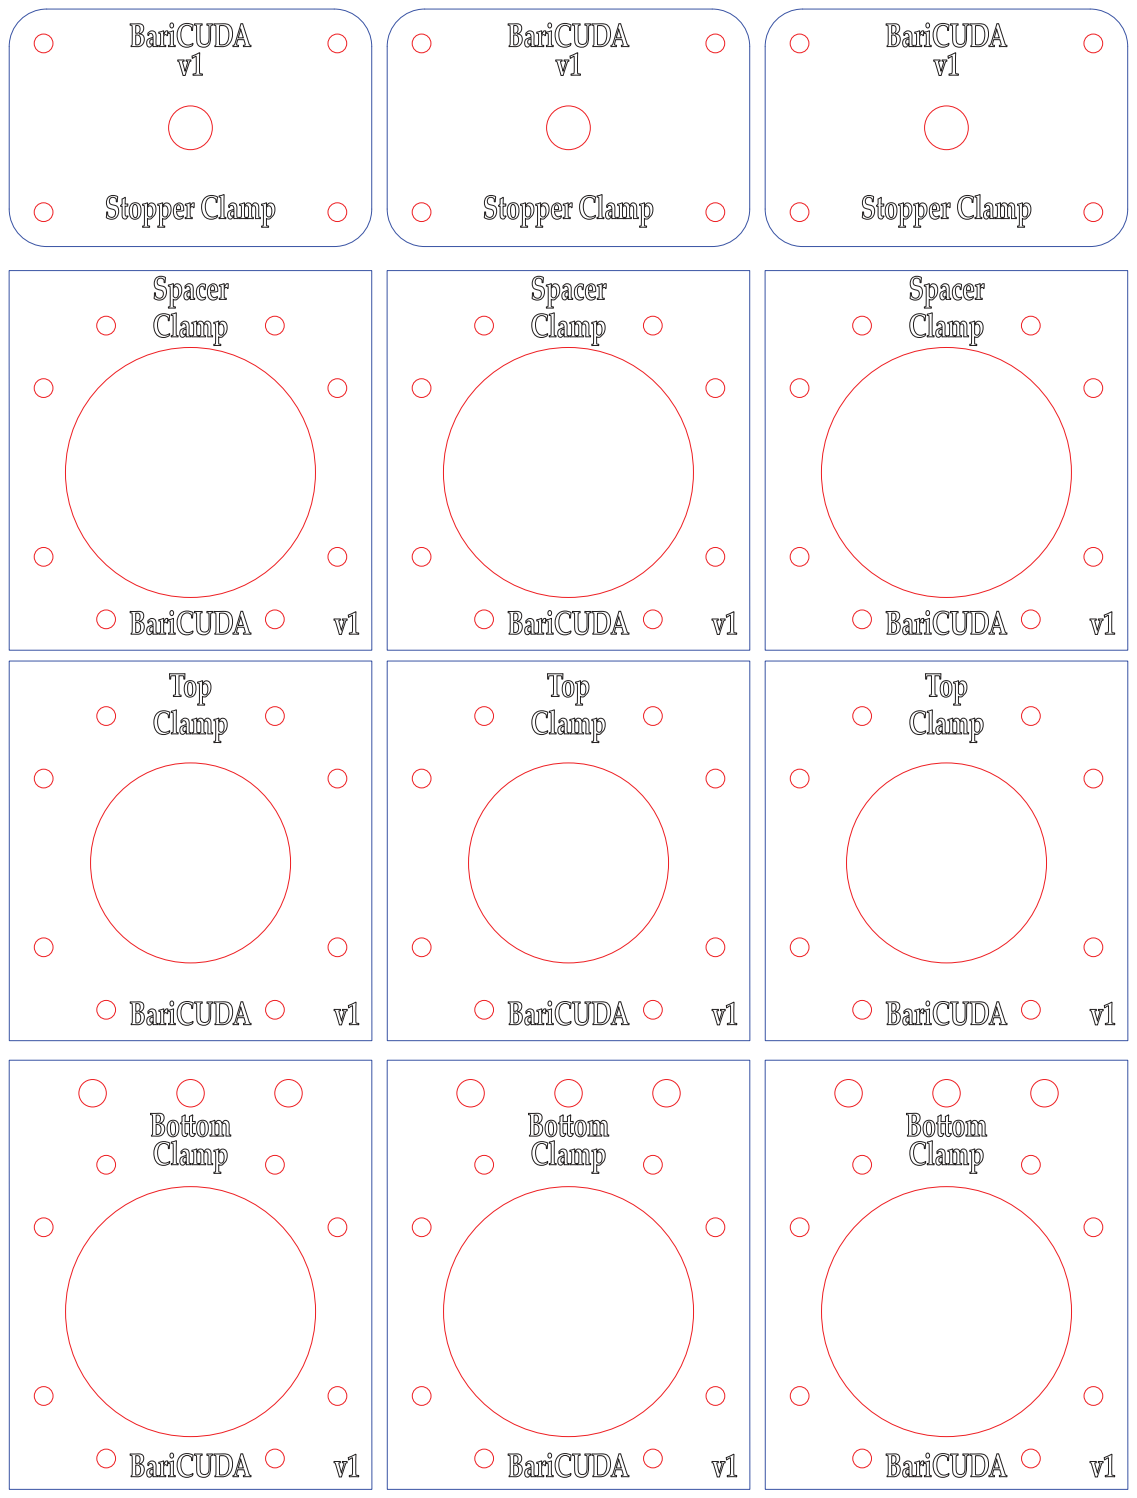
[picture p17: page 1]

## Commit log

2012-07-06 BariCUDA v1 FTW
    [BariCUDA RepRap Holder with Fan Mount.stl, CAMERAMountWithScrewHole_jmil.stl]
2012-07-06 added screenshot of lasercut clamp files
2012-08-22 if you don't have a lasercutter, you can still print these parts FTW.
    [BariCUDA RepRap Holder with Fan Mount.stl, Baricuda_v1.blend, Baricuda_v1_LaserCutParts.stl]
2013-01-30 added Modified MendelMax BOM and BariCUDA BOM. Thanks to Jordan Trachtenberg!
    [Baricuda BOM.csv, Baricuda BOM.xls, Baricuda BOM.xlsx, MendelMax BOM.csv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]
2013-05-02 adding mendelmax 1.5 parts
    [CAMERAMountWithScrewHolejmil_fixed.stl, X-carriage_slim_lm8uu_MendelMax.stl, endstop-holder_10mm.stl, endstop-holder_8mm.stl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]
2013-05-02 adding compact_mendelmax_y-rod-holders
    [jmilYRodHolderfor8mmSmoothRods.blend, jmilYRodHolderfor8mmSmoothRods4off_fixed.stl, jmilYRodHolderfor8mmSmoothRods_fixed.stl, lm8uu-holder-slim_v1-1_for8mmSmoo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]
2013-05-03 don't include gcode files. also, delete bad/old z-axis multipart files. the single-file version is way better: jmil_ImprovedZ-LowerMotorMounts.stl
    [jmilPlateMendelMax1.5ZaxisOnly_fixed.stl]
